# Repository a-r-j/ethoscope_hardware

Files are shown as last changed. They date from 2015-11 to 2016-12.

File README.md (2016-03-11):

Ethoscope Hardware
========================
This is the hardware repository of the [ethoscope platform](http://gilestrolab.github.io/ethoscope).
It contains 3d printable files and instructions that altogether should be sufficient to build ethoscopes, arenas and modules.

The software repository lives [here](https://github.com/gilestrolab/ethoscope)

Organisation
==================
This repo is organized as follows:
  1. There is a collection of folders for every part in the Ethoscope.
  2. Inside each folder there is a README file explaining the function of the part and how to put all the parts together.
  3. There is as well a folder for each sub-part.
  4. Inside each terminal folder you can find the last version of the hardware with a README explaining its function in detail.

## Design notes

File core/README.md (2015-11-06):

Ethoscope core
==============

This document describes the core of the ethoscope device.
The "core" referes to device without arena or extra modules.
it is made of three mainparts:

* the **head**, which contains the Raspebbery Pi and its camera.
* the **base**, which diffuses light though different types of arenas (read about arenas [here](../arenas/README.md)).
* the **side walls**, which simply connect the head to the base.

An assembled core looks like this:

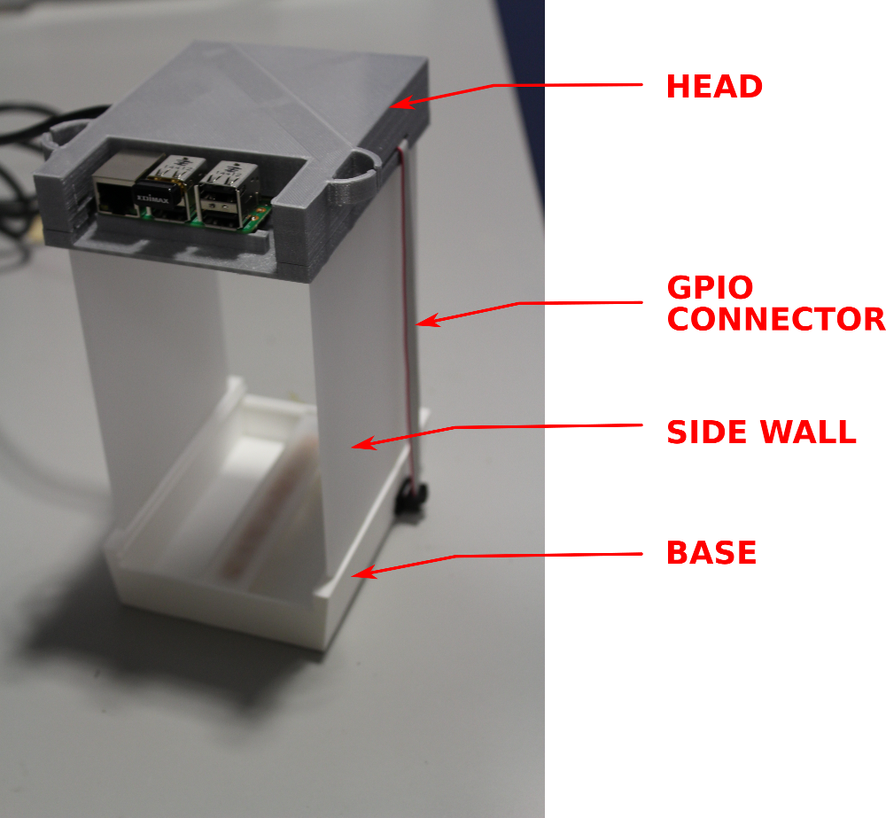
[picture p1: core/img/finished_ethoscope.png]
finished_ethoscope


Building a core
------------------

A list of all components (or BOM) is available [here](./BOM.csv).

So before we start, we should have something like:

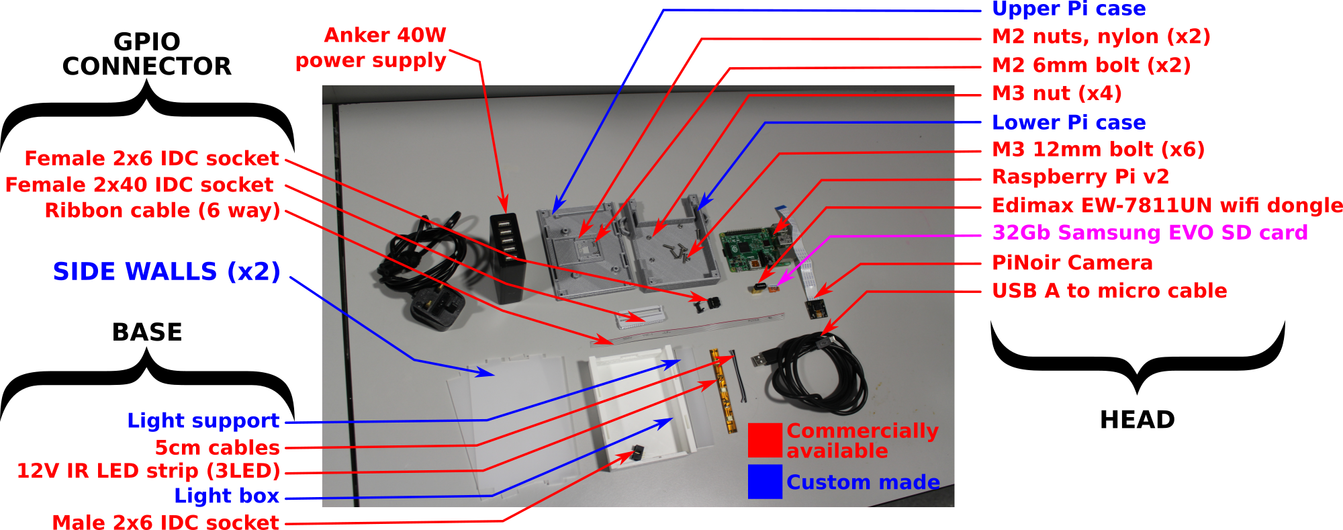
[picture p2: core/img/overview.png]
overview


In addition, you will need several tools and consumables such as:

* Allen keys
* soldering iron
* super glue
* heat shrink
* solder wire (lead free).

GPIO connector
----------------

In order to power the infrared (IR) light, the General Purpose Input Output (GPIO) of the  Raspberry Pi is connected to the base by a ribbon cable.
We can build a simple connector that looks like that:

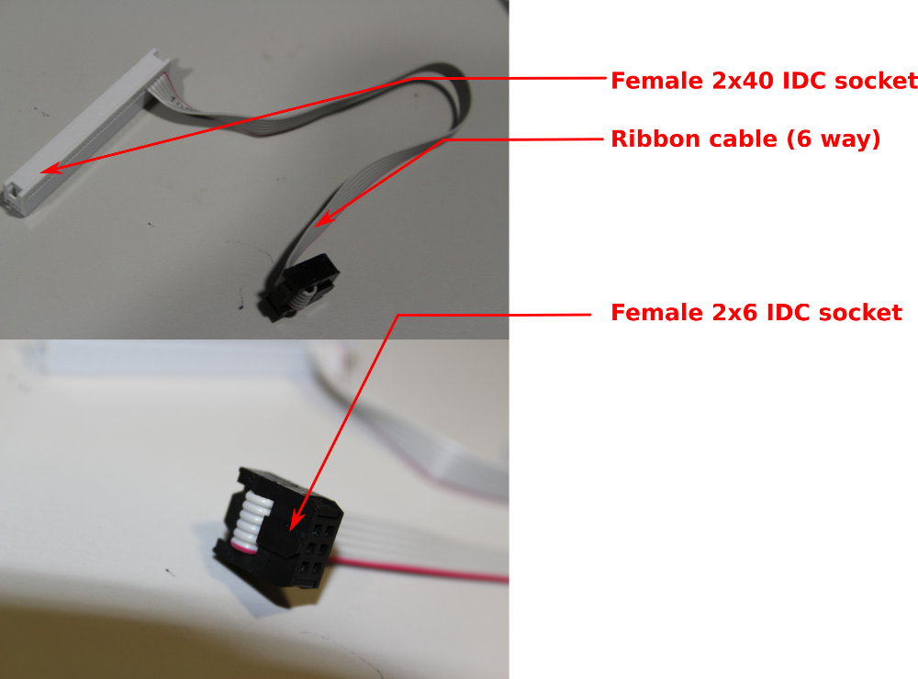
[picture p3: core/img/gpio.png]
GPIO


Here, we have used a **21cm long** 6 way ribbon cable.

Base
-----------------

The base acts as an IR light box.
The idea is to reflect IR light upward so it can go through the arena.

In order to put the light together, a little bit of basic soldering is required:

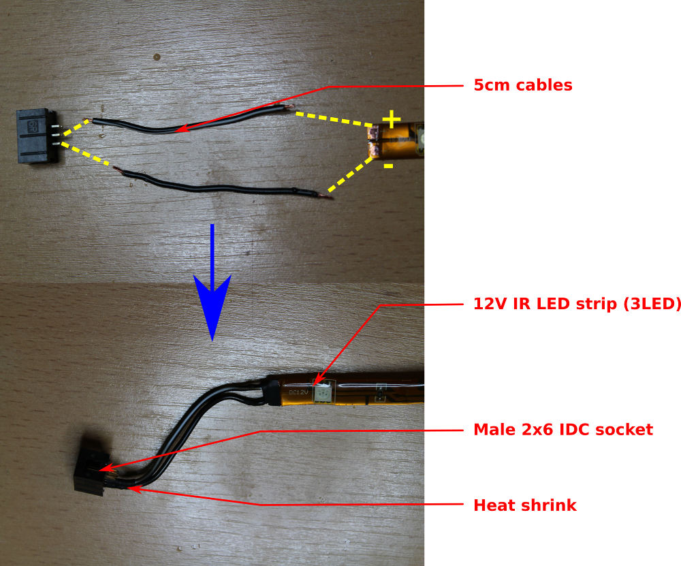
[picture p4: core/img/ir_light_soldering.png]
IR light soldering


In the figure above, the yellow dashed lined indicate where we need to solder.

You can also notice that **heat shrink** have been put around the wires so that we ensure proper insulation.

After is has been soldered, the led strip must be passed **from the outside** to the inside of the light box by the connector hole.
Then, we can stick the light to its support, and glue the support to the side of the base:

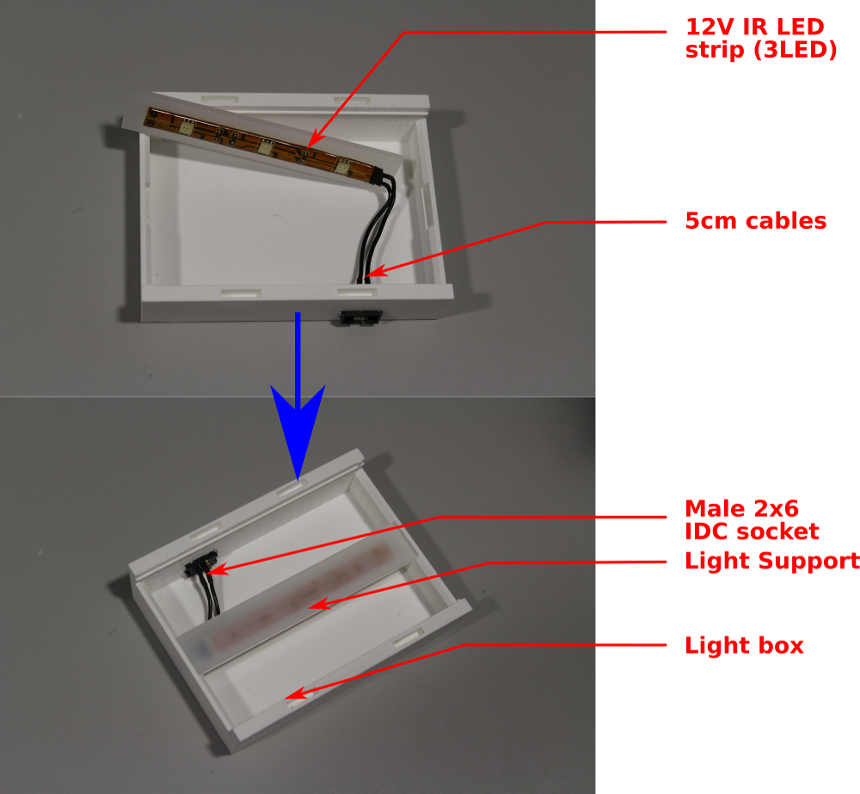
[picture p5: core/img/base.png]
base


Head
--------------------
The head is the single most important part of the device.
It is made of a Raspberry Pi, and peripherals, enclosed by pair(lower and upper) of 3d printed parts.

The steps to build the head are the following:

1. Generate a **SD card**  (it contains the operating system and all the software used by the ethoscope).
2. Plug the SD card in the Pi.
3. Place the **camera** on the lower part, and screw from the outside using M2 bolts along with the nylon nuts (sub-picture A, below).
4. Position the **Raspberry Pi** in the lower part, above the camera, and screw it from the outside, with two M3 bolts (sub-picture B, below).
5. Connect the camera, the **GPIO connector** and the wireless dongle to the Pi.
6. In the upper part, there are four holes in the corners. They allow us to close the box with screws. You want to **insert a nut in each slit** under the hole,
7. Now, we can **close the box** (sub-picture C, below) and screw the upper and lower parts together, using four M3 screws.
8. The last thing we want to do is plugging the micro-usb power supply in the Pi.

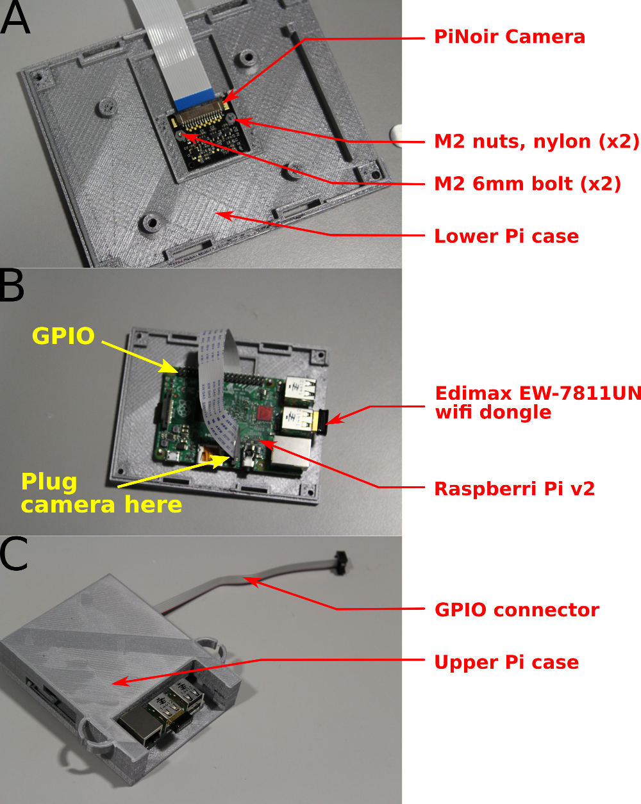
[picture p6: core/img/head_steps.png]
Head steps


Last bits:
Before you can start working, you will have to **change the focus of the camera**.
I am afraid this has to be done manually. A very good explanation is available here(TODO).

The wireless dongle blinks with blue light to indicate that it transmits data. 
According to your expoerimental setup, you may want to blind the LED (e.g. with black tape) in order to prevent interference with the behaviour of your experimental animals.

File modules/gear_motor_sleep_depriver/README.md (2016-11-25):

Gear Motor Sleep Depriver
==========================

This document describes the geared motor sleep depriver module for the ethoscope.
It is based on based on GM23s, controled by a roboRED board.
The Onshape project lives [here](https://cad.onshape.com/documents/3d4348ea20384ce925691583/w/6966f4288591c2cdd19df81a/e/d6ee913fc9f5ea86d3caff62)

It is made only of one part.
An assembled module looks like this:

finished_sdgm

Building this module
----------------------

A list of all components (or BOM) is available [here](./BOM.csv).

First, you will need to compile and upload the firmware onto the arduino board usiong the [ino file](gear_motor_sd.ino).

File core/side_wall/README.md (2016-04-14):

Side Walls
============

Side walls are laser cut in 3mm, mat, transparent perspex acrylic.
The svg and PDF can be use with most laser cutter.

The side Perspex  we are using is s030 polar white and the piece should be 300*600 mm if you want to use the PDF and lasser cut.
A provider in london is www.hamaracrylic.co.uk/hamar_acrylic_fabrications.aspx

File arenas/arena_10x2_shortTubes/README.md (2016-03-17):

---
Name: 10x2 short tubes arena
Authors: Luis Garcia, Quentin Geissmann
Number of regions: 20
Size: standard
Description: >
            This arena is designed to study movement of 20 flies in 5mm x 3mm x 65mm (outside diam., inside diam., length) 
            tubes. It mimicks conditions in conventional Trikinetics activity monitoring device.
              
---

[Preview](arena_10x2_shortTubes.stl)

Manufacture
-------------
3d Printed in ABS/PLA/NYLON

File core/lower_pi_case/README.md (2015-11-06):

Lower Pi Case
============

This 3d printed part hold the camera in place and encloses the Raspberry Pi.

Have a look at the [3d preview](lowerPiCase.stl).

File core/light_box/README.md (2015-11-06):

Light Box
============

This 3d printed part diffuses light (most likely IR light) through the arena.

Have a look at the [3d preview](lightBox.stl).

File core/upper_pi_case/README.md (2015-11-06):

Upper Pi Case
============

This 3d printed part encloses the Raspberry Pi.

Have a look at the [3d preview](upperPiCase.stl).

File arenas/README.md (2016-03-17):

Arenas
==================

Arenas are a crucial part of experimental design using the ethoscope platform.

An arena is physical translation of an experimental paradigm.

With the ethoscope platform, it is possible to work with multiple arenas according to your biological question and model organism.

Arenas are generally 3d printed and can be derived from templates.
template arena have the suffix **"template"**

There are several conventional sizes of arena that corresponds to the camera mode of the ethoscopes.
namely, the sizes:

* standard 
* *mini* (the keyword mini is in the name of these arenas)

The mini arenas have smaller surfaces and are optimises for HD video acquisition.
The standard size is a good compromise between image surface and time resolution allowing users to perform real time tracking

Adding new arenas
--------------------------

When adding new arena. Please, provide:

* A Readme with a description (and and name, author, number of rois,...)
* An stl file
* A 1min mp4 video of the arena with animals. It can be done with `ffmpeg` (e.g. `ffmpeg -ss 00:01:00 -i input.mp4  -t 00:01:00  -c:v libx264 -preset veryslow -crf 26  arena_xxx_xxx.mp4`)

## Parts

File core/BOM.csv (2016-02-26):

Piece | Part | Quantity | Supplier | Reference | Price
Lower Pi case | Head | 1 | Polygonal Tree/Custom made | https://github.com/gilestrolab/ethoscope_hardware/tree/master/core/upper_pi_case | £1
Upper Pi case | Head | 1 | Polygonal Tree/Custom made | https://github.com/gilestrolab/ethoscope_hardware/tree/master/core/lower_pi_case | £1
Raspberry Pi v2 | Head | 1 | CPC |  | £20
PiNoir camera | Head | 1 | RS | RS 790-2811 | £12
32Gb SD card | Head | 1 | amazon | 32G Samsung EVO SD card | £8
M3 12mm bolt | Head | 6 | RS | RS 232-8372
M3 nuts | Head | 4 | RS | RS 560-293
M2 nuts (nylon) | Head | 2 | RS | RS 528-126
M2 6mm bolts | Head | 2 | RS | RS 482-7685
Wifi dongle | Head | 1 | Edimax | Edimax EW-7811UN | £8
Light box | Base | 1 | Polygonal Tree/Custom made | https://github.com/gilestrolab/ethoscope_hardware/tree/master/core/light_box | £1
Light support | Base | 1 | Polygonal Tree/Custom made | https://github.com/gilestrolab/ethoscope_hardware/tree/master/core/side_wall | £1
Male 2x6 IDC socket | Base | 1 | RS | RS 832-3496
12V IR LED strip | Base | 3LED | Lightworld | http://www.ledlightsworld.com/infrared-led-strips-c-1_79.html | £1
5cm cable | Base | 2 | RS
Side wall | Side Wall | 2 | Polygonal Tree/Custom made | https://github.com/gilestrolab/ethoscope_hardware/tree/master/core/side_wall | £2
Ribbon cable (6 way; 21cm) | GPIO connector | 1 | RS | RS 693-7699
Female 2x6 IDC socket | GPIO connector | 1 | RS | RS 832-3648
Female 2x40 IDC socket | GPIO connector | 1 | RS | RS 625-7303
USB A to micro cable | Power supply | 1 | RS | RS 888-8811
Anker 40w PSU | Power supply | 1 | Amazon |  | £12

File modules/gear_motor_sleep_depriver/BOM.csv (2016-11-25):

Piece | Part | Quantity | Supplier | Reference | Price
Main box | main | 1 | Polygonal Tree/Custom made | https://github.com/gilestrolab/ethoscope_hardware/tree/master/gear_motor_sleep_depriver/TODO
Box clips | main | 2 | Polygonal Tree/Custom made | https://github.com/gilestrolab/ethoscope_hardware/tree/master/gear_motor_sleep_depriver/TODO
Shafts | main | 10 | Polygonal Tree/Custom made | https://github.com/gilestrolab/ethoscope_hardware/tree/master/gear_motor_sleep_depriver/TODO
RoboRED | main | 1 | yourduino.com | http://yourduino.com/sunshop//index.php?l=product_detail&p=429 | 15$
GM23 gear motor | main | 10 | solarbotics.com | https://solarbotics.com/product/gm23/ | 4$
Female 3 pins crimps | main | 10 | RS
Crimps stuff | main | 20 | RS
Ribbon cable
Silicon tubing 6x9 mm
Push button (optional)
USB A to mini cable | main | 1 | RS

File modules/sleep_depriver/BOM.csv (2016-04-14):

Piece | Part | Quantity | Supplier | Reference | Price
USB A to micro cable | Power supply | 1 | RS | RS 888-8811
Anker 40w PSU | Power supply | 1 | Amazon | ? | £12
Base | Base | 1 | 3d printed | ? | low
Lynx Motion SSC-32 Servo Controller | servo controller | 1 | robotshop | http://robotshop.com/en/lynxmotion-ssc-32-servo-controller.html | £25.00
USB A to mini cable (30cm) | Serial mini USB connector | 1 | amazon | http://www.amazon.com/30CM-male-plug-leads-Cable/dp/B00MMVLH9I | low
9G micro servo | Servo | 10 | robotshop | ? | ?
2x6mm screw | Pulley screw | 10 | Amazon | http://www.amazon.co.uk/Tapping-Thread-Round-Phillips-Screw/dp/B00GMQDSRI | low
Pulley | Pulley | 10 | 3d printed | ? | low
22mm x1.5mm cs nitrile black o-ring | O-ring | 10 | polymax.co.uk | https://www.polymax.co.uk/o-ring-22mm-id-x-1-5mm-cs-nitrile-black-70-sha | low
2x10mm screw | Servo screw | 20 | Amazon | http://www.amazon.co.uk/dp/B00MFBTWMO/ref=pe_385721_37986871_TE_item | low

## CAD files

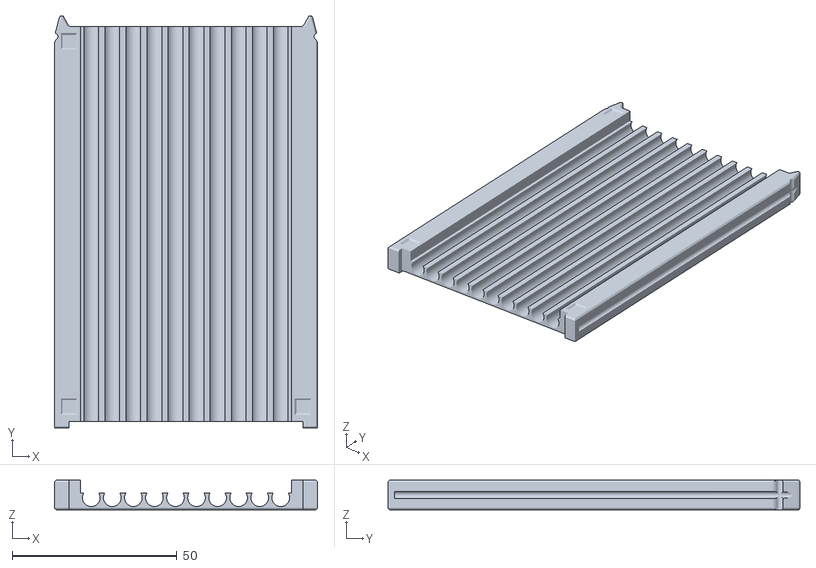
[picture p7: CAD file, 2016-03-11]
arenas/arena_10x1_longTubes/arena_10x1_longTubes.stl
80.0 x 125.2 x 9.00

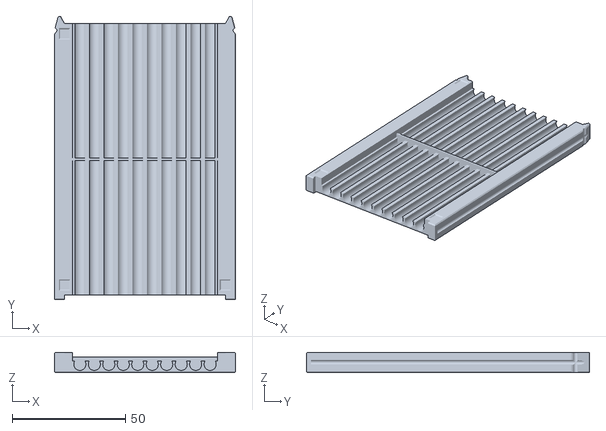
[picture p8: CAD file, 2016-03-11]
arenas/arena_10x2_shortTubes/arena_10x2_shortTubes.stl
80.0 x 125.2 x 9.00

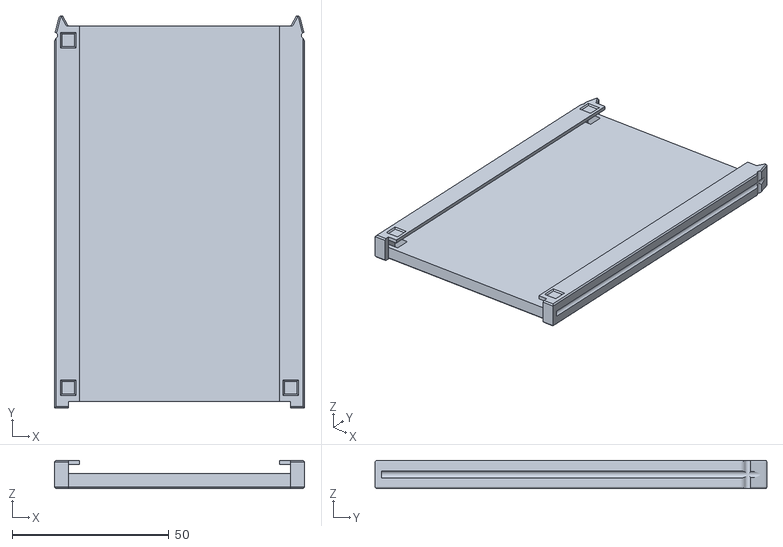
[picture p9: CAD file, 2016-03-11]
arenas/arena_glassLid_template/arena_glassLid_template.stl
80.0 x 125.2 x 9.00

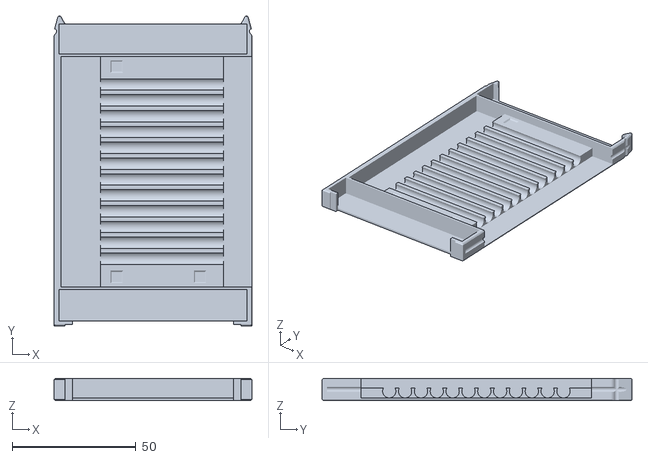
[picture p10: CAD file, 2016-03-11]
arenas/arena_mini_12_tubes/arena_mini_12_tubes.stl
80.0 x 125.2 x 9.00

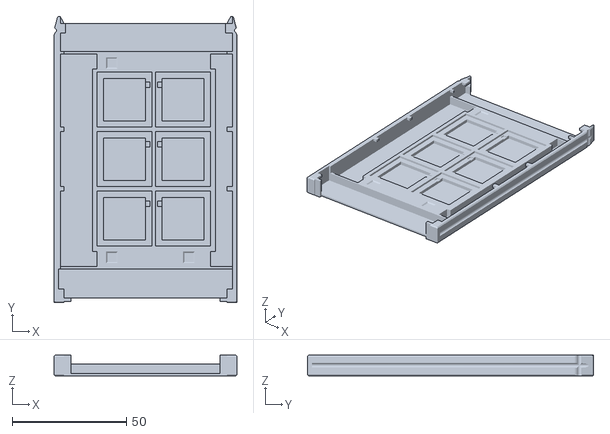
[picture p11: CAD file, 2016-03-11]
arenas/arena_mini_squares/arena_mini_squares.stl
80.0 x 125.2 x 9.00

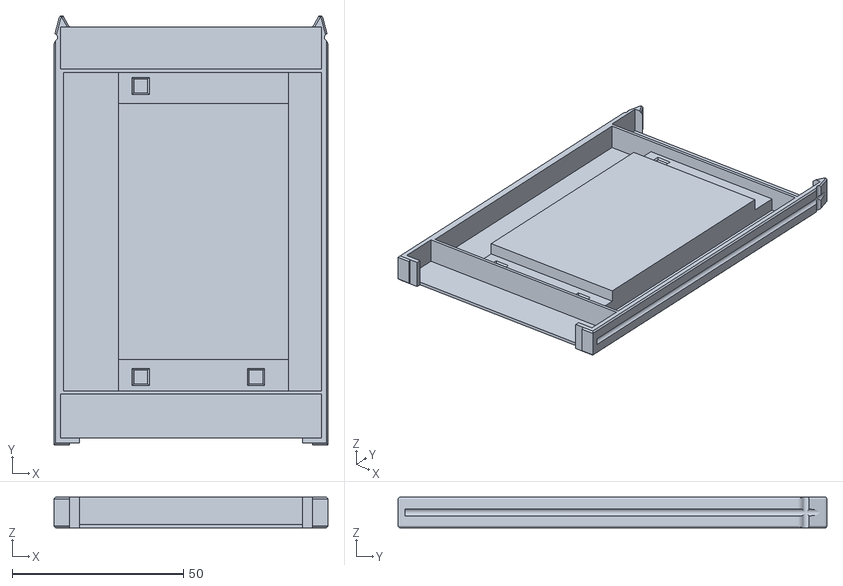
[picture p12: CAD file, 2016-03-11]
arenas/arena_mini_template/arena_mini_template.stl
80.0 x 125.2 x 9.00

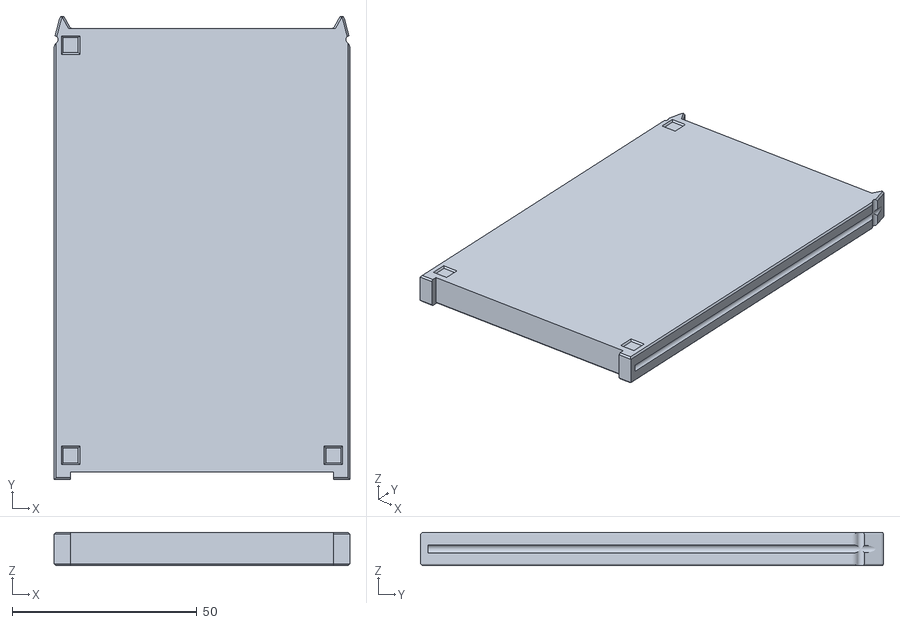
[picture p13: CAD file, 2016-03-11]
arenas/arena_template/arena_template.stl
80.0 x 125.2 x 9.00

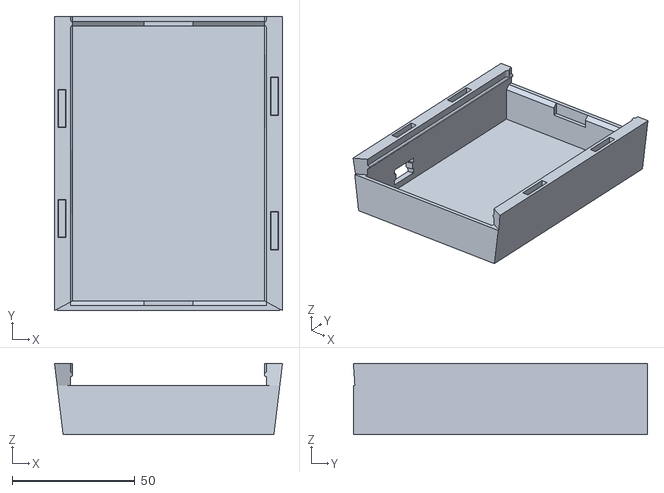
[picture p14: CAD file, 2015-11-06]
core/light_box/lightBox.stl
93.0 x 120.0 x 29.0

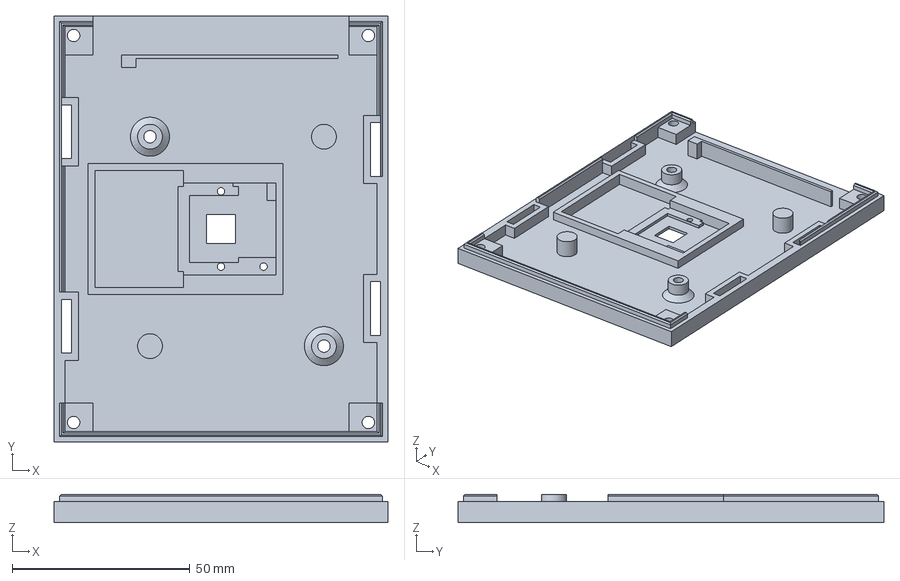
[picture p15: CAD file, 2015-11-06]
core/lower_pi_case/lowerPiCase.step
94.0 x 120.0 x 8.00 mm

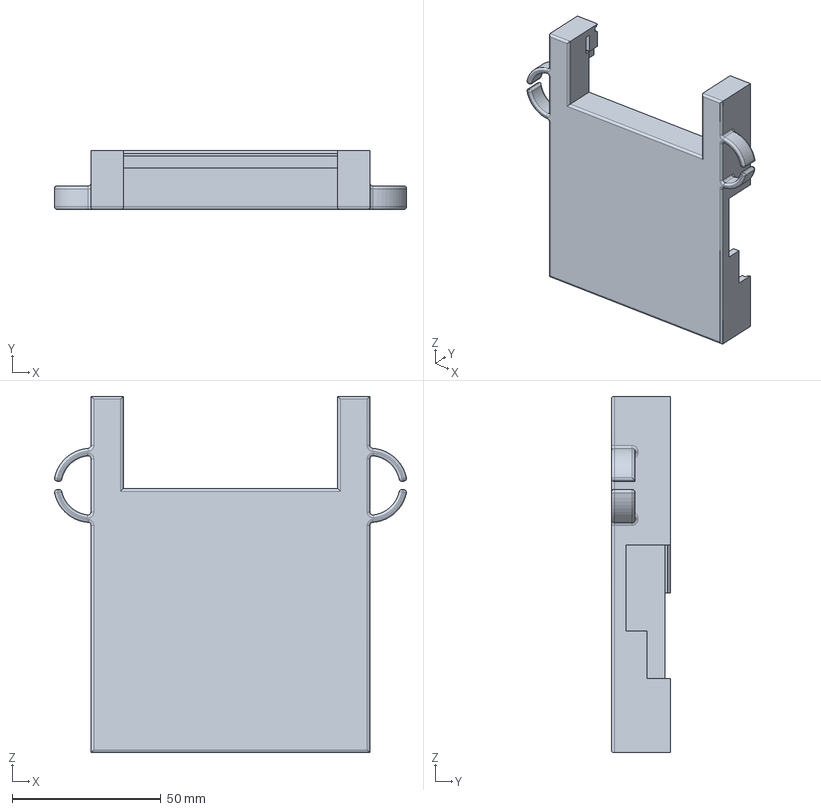
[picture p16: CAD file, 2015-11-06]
core/upper_pi_case/upperPiCase.step
118.5 x 20.0 x 120.0 mm

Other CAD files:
arenas/arena_sdModule/arena_sdModule.stl
arenas/arena_squares/arena_squares.stl
core/light_box/core_lightBox.step
core/lower_pi_case/lowerPiCase.stl
core/upper_pi_case/upperPiCase.stl

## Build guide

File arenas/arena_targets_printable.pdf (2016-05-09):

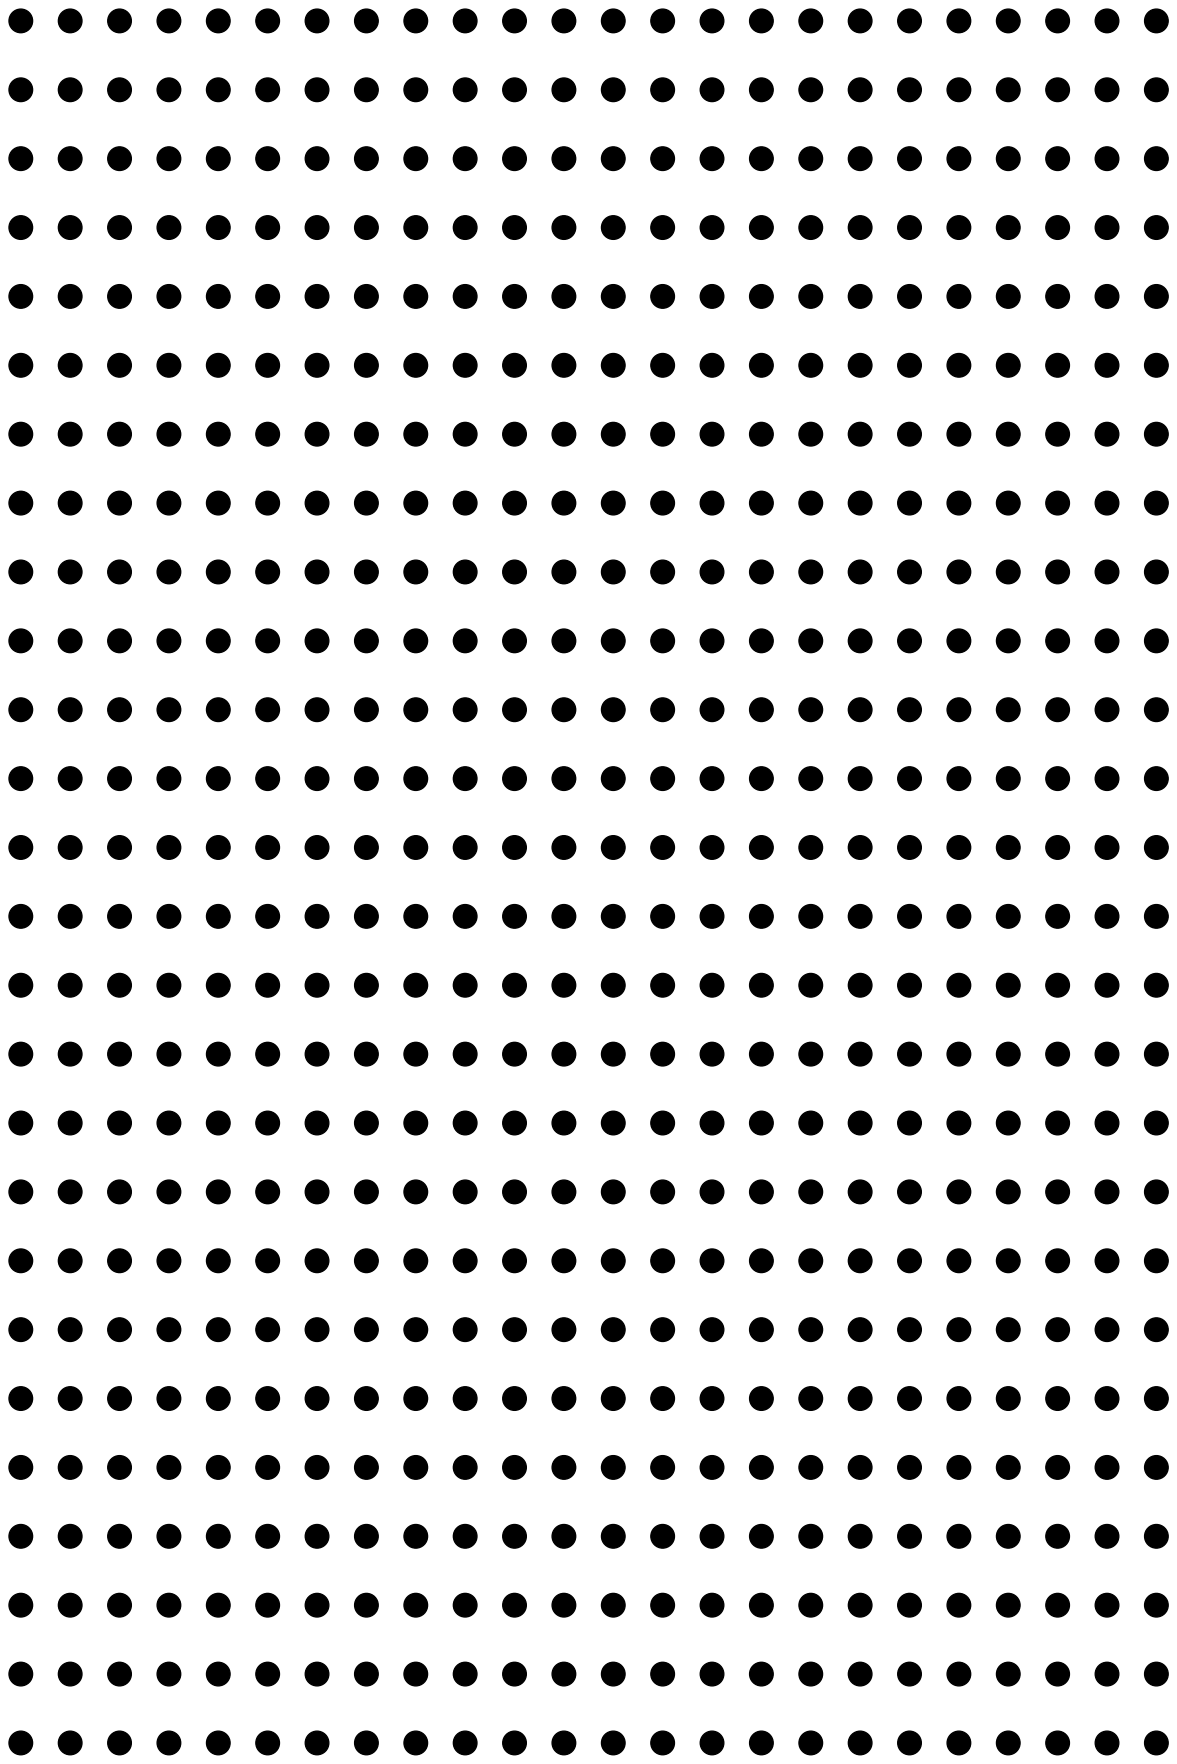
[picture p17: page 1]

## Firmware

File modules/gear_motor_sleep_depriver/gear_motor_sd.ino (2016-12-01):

/* Program using Adafruit TLC5947 to control up to 24 components with pwm.
 *  Usage:
 *  
 * P CHANNEL DURATION(ms) [INTENSITY](0-1000)
 * 
 * CHANNEL is a componenet from 0 to 23.
 * DURATION defines how long this compoenet is to be activated for (in ms)
 * INTENSITY is the duty cycle of the PWM  (optional, from 0 to 1000)
 * 
 * example:
 * P 2 1000
 * P 0 1000 500
*/


#include <SoftwareSerial.h> 
#include <SerialCommand.h>
#include <Adafruit_TLC5947.h>


#define BAUD 115200
#define N_OUTPUTS 24

// a set of timers measuring how long a given output should remain on for
int timers[N_OUTPUTS] = {0};
// stores the PWM of each output
unsigned int pwms[N_OUTPUTS];

unsigned long t0 = 0;
unsigned long t1 = 0;

SerialCommand SCmd;

/* ======================== TLC 5947 ======================== */
#define NUM_TLC5974 1

#define MAX_PWM 4095   
#define MIN_PWM 0   

// Define Pinouts from Arduino to SPI pins on LED Driver Board
#define TLC_DATA_PIN 3
#define TLC_CLOCK_PIN 4
#define TLC_LATCH_PIN   6
//#define oe  -1  // set to -1 to not use the enable pin (its optional)

Adafruit_TLC5947 tlc = Adafruit_TLC5947(NUM_TLC5974, 
                                        TLC_CLOCK_PIN,
                                        TLC_DATA_PIN,
                                        TLC_LATCH_PIN);

/* ======================== Push button======================== */

#define PUSH_BUTTON_PIN 5
// how long (in ms) the push buton should be hold for before demo is run
#define PUSH_BUTTON_THR 2000
// a timer that records how long push button is pressed for
int push_button_timer = 0; 




void setup() {
  Serial.begin(BAUD);
  SCmd.addCommand("P",sendPWMSerial);  
  SCmd.addCommand("D",demo);  
  SCmd.addCommand("H",help);
  //SCmd.setDefaultHandler(help);  
  
  tlc.begin();
  
  for (unsigned int i = 0; i != N_OUTPUTS; ++i){
    pwms[i] = 0;
    timers[i] = 0;
    tlc.setPWM(i,0);
  }
  tlc.write();

  pinMode(PUSH_BUTTON_PIN, INPUT);
}

void help(){
  Serial.println("P CHANNEL DURATION(ms) [INTENSITY](0-1000)");
  }
void loop() { 
  SCmd.readSerial(); 
  delay(50);
  t0 = t1;
  t1 = millis();
  
  //fixme overflow of time!
  // i.e. if t0 > t1
  unsigned int tick =  t1 - t0;

  for (unsigned int i = 0; i != N_OUTPUTS; ++i){
    if(timers[i] != 0){
       timers[i] -= tick;
       if(timers[i] <0){
        timers[i] = 0;
        tlc.setPWM(i,MIN_PWM);
        tlc.write();
      }
    }
  }
  if(digitalRead(PUSH_BUTTON_PIN) == LOW){
    if(push_button_timer > PUSH_BUTTON_THR)
        demo();
    push_button_timer = 0;
  }
    
  else{
    push_button_timer += tick;
      
  }
}


void sendPWM(unsigned int idx, unsigned int duration, unsigned int duty_cycle = MAX_PWM){
  timers[idx] = duration; // in ms
  tlc.setPWM(idx,duty_cycle);
  tlc.write();
}

void demo(){
  for (unsigned int i = 0; i != N_OUTPUTS; ++i){
    tlc.setPWM(i,MAX_PWM);
    tlc.write();
    delay(500);
    tlc.setPWM(i,MIN_PWM);
    tlc.write();
  }
}

void sendPWMSerial(){
  char *arg;
  arg = SCmd.next();  
  unsigned int motor_id = 0;
  unsigned int duration = 0;
  unsigned int duty_cycle = MAX_PWM;
  unsigned int power = 0;
  
  if (arg != NULL) 
    motor_id = atoi(arg) ;
  else
   return; 
   
  arg = SCmd.next();   
  if (arg != NULL)
    duration = atoi(arg) ;
  else
    return;
  
  arg = SCmd.next();   
  if (arg != NULL){
    power = atoi(arg);
    duty_cycle = ((uint32_t)  power * (uint32_t) MAX_PWM)/1000;;
  }
  sendPWM(motor_id, duration, duty_cycle);
  }

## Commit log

2015-07-14 initial commit, added arenas
    [arena_clean.stp, arena_empty_for_extrusion.stp, arena_for_tubes_2.0.stl, arena_for_tubes_2.0.stp]
2015-09-02 arena 20 tubes
    [arena_clean.stp, arena_empty_for_extrusion.stp, arena_for_tubes_2.0.stl, arena_for_tubes_2.0.stp]
2015-09-02 readme add
    [20_tubes_arena.step, 20_tubes_arena.stl, arena_clean.stp, arena_empty_for_extrusion.stp]
2015-09-22 new 20 tubes arena
    [20_tubes_20150922.stl, 20_tubes_arena.stl]
2015-10-28 add BOM
    [BOM_Ethoscope.csv, arena_clean.stp, arena_empty_for_extrusion.stp]
2015-10-28 walls svg laser cutter
2015-11-05 write doc on how to build an ethoscop. draft
    [BOM.csv]
2015-11-06 put step files online
    [BOM.csv, core_lightBox.step, lowerPiCase.step, upperPiCase.step]
2015-11-06 add stl files
    [lightBox.stl, lowerPiCase.stl, upperPiCase.stl]
2015-11-06 updated BOM for RS screews
    [BOM.csv]
2016-02-01 Updated part number for female light connector
    [BOM.csv]
2016-02-26 Adding approximate prices
    [BOM.csv]
2016-03-11 add new arenas/backup onshape
    [20_tubes_20150922.stl, 20_tubes_arena.step, arena_10x1_longTubes.stl, arena_10x2_shortTubes.stl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]
2016-11-22 add prototype of gmsd firmware
2016-11-25 instructions for the new SD ++
    [BOM.csv]
2016-11-29 use TLC5947 to control gear motor as well as LEDs
